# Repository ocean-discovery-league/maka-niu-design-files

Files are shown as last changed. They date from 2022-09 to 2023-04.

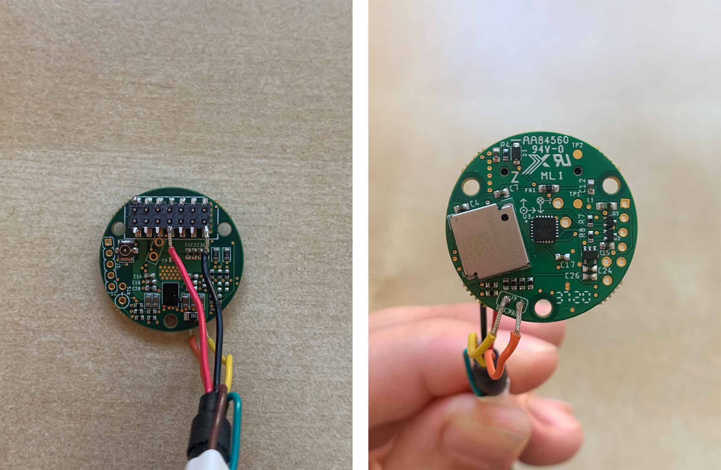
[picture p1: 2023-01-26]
Circuit_Boards/endcap/GNSS_AND_IMU_FIX/GNSS_Flashing_Example.jpg

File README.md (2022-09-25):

# maka-niu-design-files
All files needed to build a Maka Niu

Instructions for fabrication and software installation here.

Link to install image here.
 
Please direct all questions concerning fabrication plans or direct purchase of the Delrin housing to Dr. Allan Adams of Oceanic Labs (allan@oceanic-labs.org)

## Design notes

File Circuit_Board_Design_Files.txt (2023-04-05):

To build a Maka Niu Camera system, you will need to acquire a Pi Zero W or a Pi Zero 2W
Additionally, you will need to acquire or fabricate the following custom PCBs

-Endcap PCB
-Battery Management PCB
-Pi Zero Shield
-Hall Sensor Board (aka Hall Ring)

To build a Maka Niu LED module, you will need to acquire a Pi Zero W or a Pi Zero 2W
Additionally, you will need to acquire or fabricate the following custom PCBs

-Endcap PCB
-Battery Management PCB
-Pi Zero Shield
-Hall Sensor Board (aka Hall Ring)
-LED PCB

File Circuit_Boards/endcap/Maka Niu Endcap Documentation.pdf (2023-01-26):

### Maka-Niu Endcap PCB

The endcap PCB is a 6-layer, 26mm diameter board that handles wireless Qi charging, GPS (including external antenna connector), IMU, and breakouts for the Keller pressure sensor and for an external thermistor to provide temperature-related shutdown capability.

The endcap PCB connects to the other PCBs in the stack via a 14 pin Molex connector.

The wireless charging IC is an IDT P9221-R. The datasheet can be found here: https://www.mouser.com/datasheet/2/464/IDT_P9221-R-Datasheet_DST_20171010-1093280.pdf (https://www.mouser.com/datasheet/2/464/IDT_P9221-R-Datasheet_DST_20171010-1093280.pdf)

The GPS module is an AirPrime XM1110. The most recent datasheet must be requested from Sierra Wireless.

The IMU is a TDK InvenSense ICM-20948 9-axis IMU. The datasheet can be found here: https://invensense.tdk.com/wp-content/uploads/2016/06/DS-000189-ICM-20948-v1.3.pdf

Following are the layouts of the top and bottom of the board:

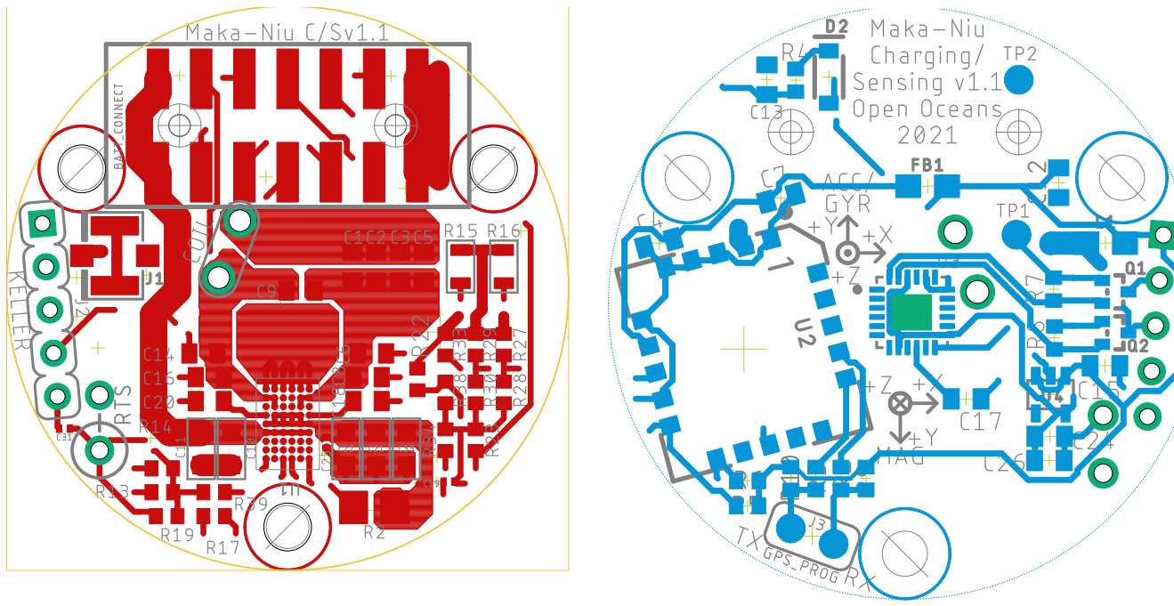
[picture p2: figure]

Top of board, important details

The pinouts for the 14 pin Molex connector are as follows:

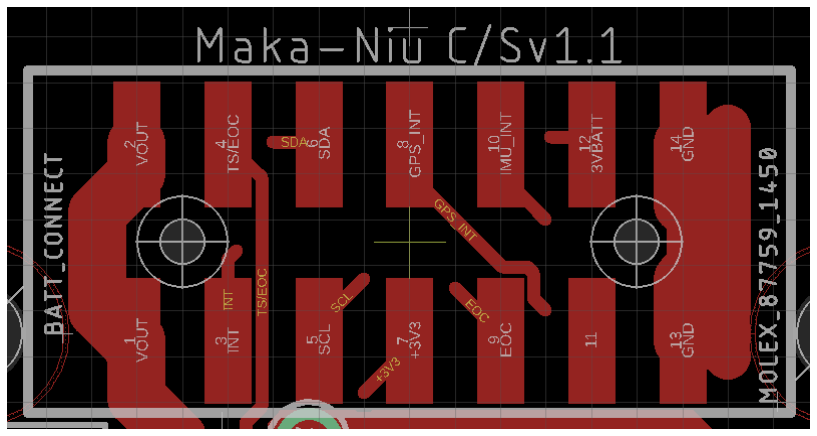
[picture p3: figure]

Pins numbered according to columns left to right and rows bottom to top within columns (as shown in diagram above, viewed in this orientation):

1: VOUT (to main battery)
2: VOUT (to main battery)
3: !INT (for wireless charger)
4: TS/EOC (temperature sensing/end of charge for wireless charger) 5: SCL
6: SDA
7: +3.3V
8: GPS INTERRUPT
9: EOC (from Keller pressure sensor) 10: IMU INTERRUPT
11: unused
12: 3V BACKUP BATTERY (for GPS)
13: GND (common)
14: GND (common)

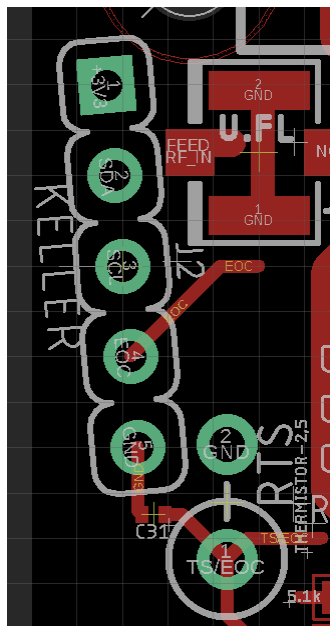
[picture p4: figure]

The pinouts for the Keller pressure sensor and the thermistor are as follows:

For the Keller sensor, where pin 1 has the square pad:

1: +3.3V
2: SDA
3: SCL
4: EOC
5: GND

For the thermistor, where pin 1 is circled:

1: TS/EOC
2: GND

Here is the ECAD layout of the full top of the board:

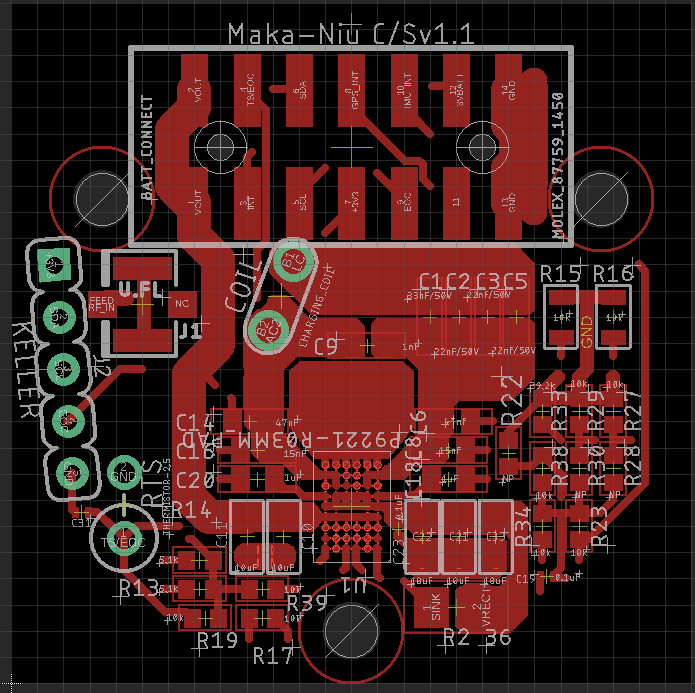
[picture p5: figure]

Important programming resistors to note in the resistor cluster to the bottom right:

R22: used as part of a resistor divider for setting the overcurrent limit (ILIM)
R28: used as part of a resistor divider for tuning foreign object detection (FOD); tunes received packet power gain (RPPG)
R30: used as part of a resistor divider for tuning foreign object detection (FOD); tunes received packet power offset (RPPO)

These resistors are unpopulated in the initial assembly.

Here is a photograph of the prototype assembly. The unpopulated resistors are visible in the lower right, although they are not labeled on the silkscreen. They will be labeled in the final production run.

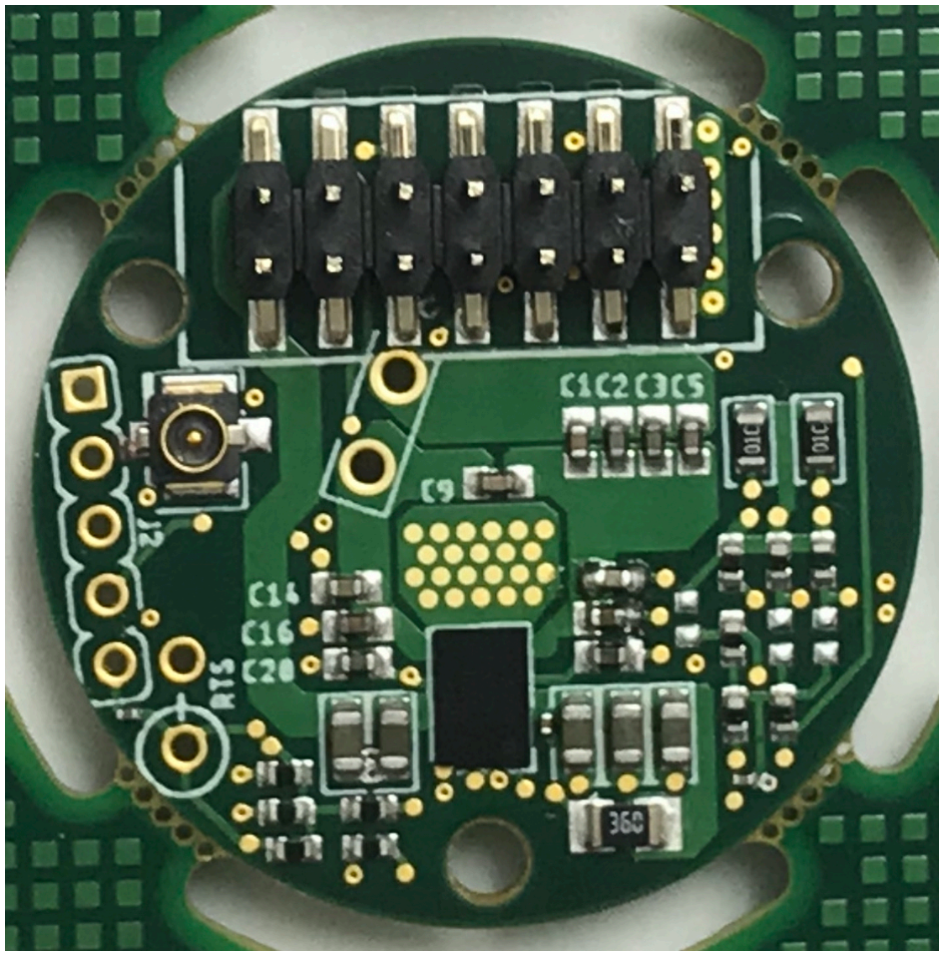
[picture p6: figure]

Bottom of board, important details

The bottom of the board contains the GPS module and the IMU. The important features for manual adjustment/testing are J3, the GPS programming connector, and the two electrical testpoints TP1 and TP2.

Here is the ECAD layout of the bottom of the board:

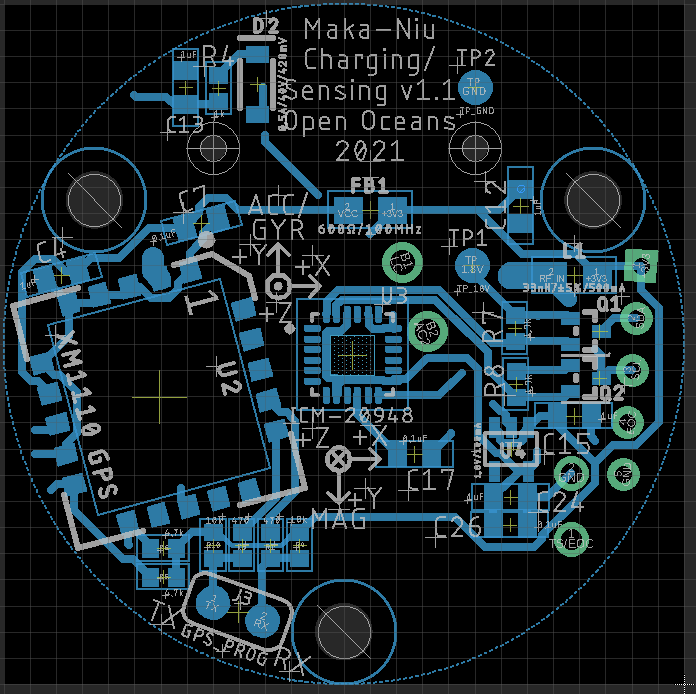
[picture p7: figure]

As can be seen from this image, J3 has TX on the left and RX on the right.

The expected testpoint voltages are as follows:

TP1: +1.8V
TP2: GND

Here is a photograph of the prototype assembly. Note that TX and RX are unlabeled in the silkscreen; they will be labeled in the final production run. Note also that the GPS module is 180° rotated from its correct orientation; this photograph was taken before this assembly error was corrected. It will be correctly oriented in the production run.

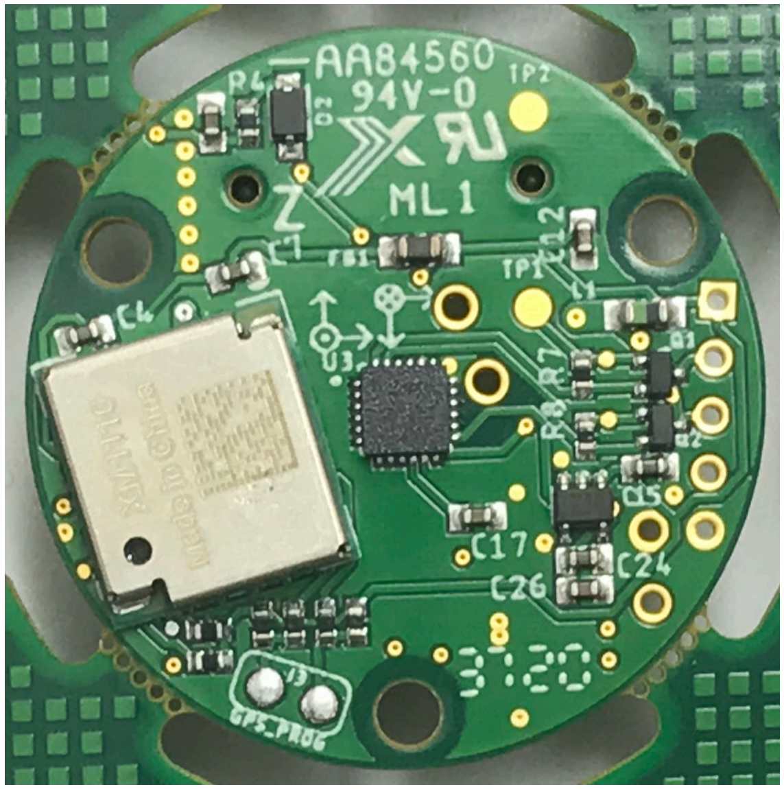
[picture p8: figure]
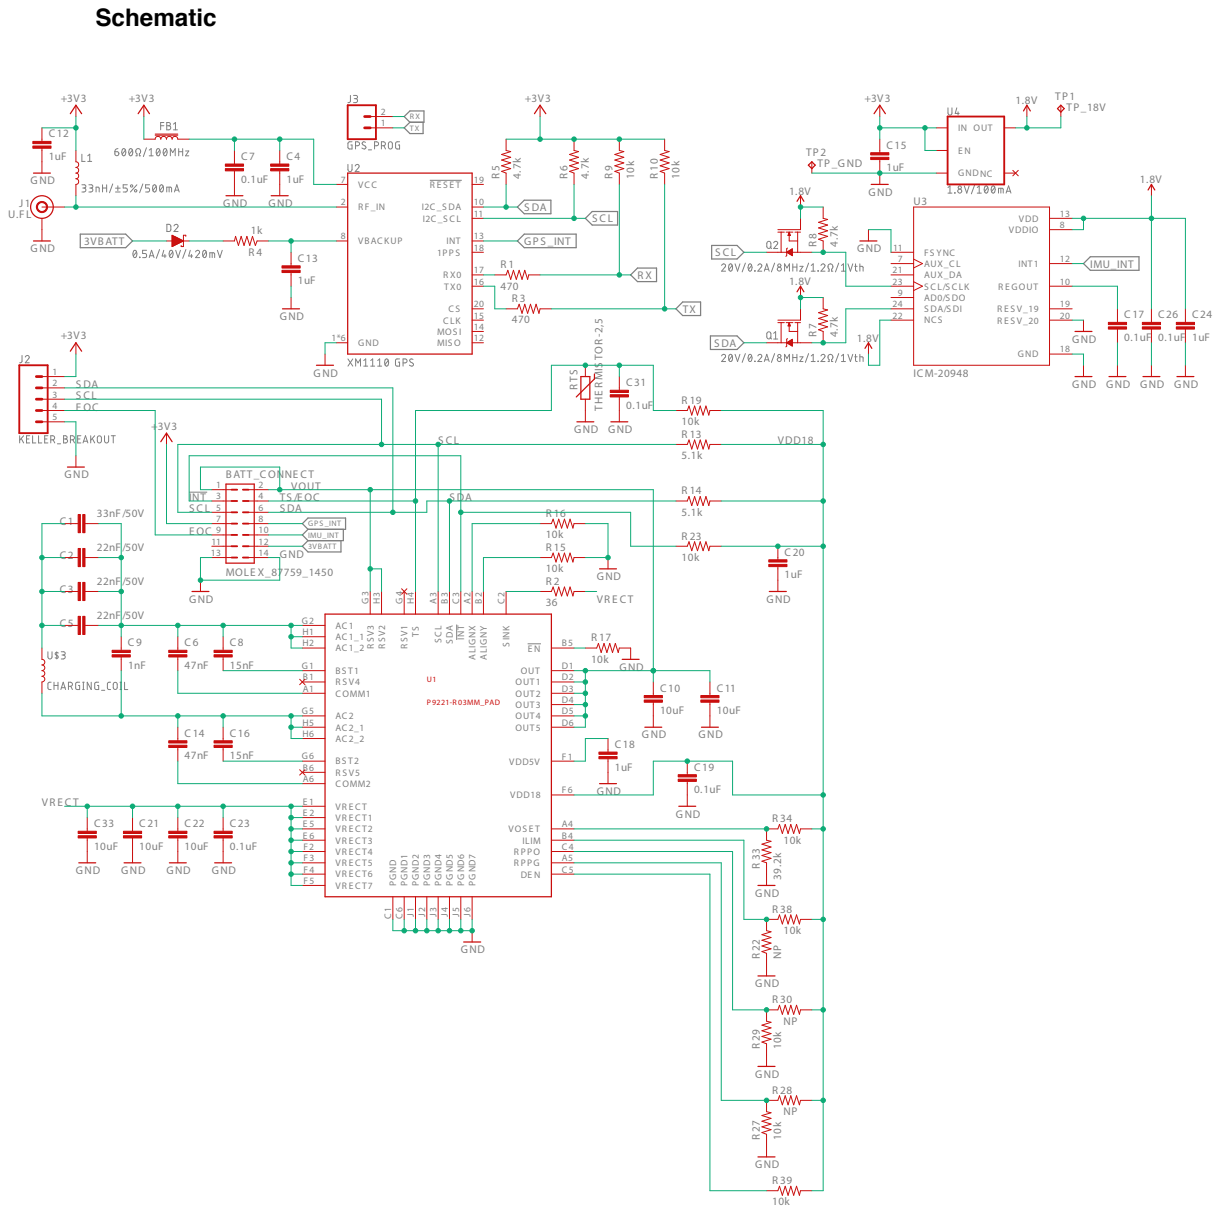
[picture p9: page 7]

GND GND

BS T1 G1 | 10k GND
R S V4 B1 COMM1 A1 | | GND

AC2_1 H5
AC2_2 H6 | GND

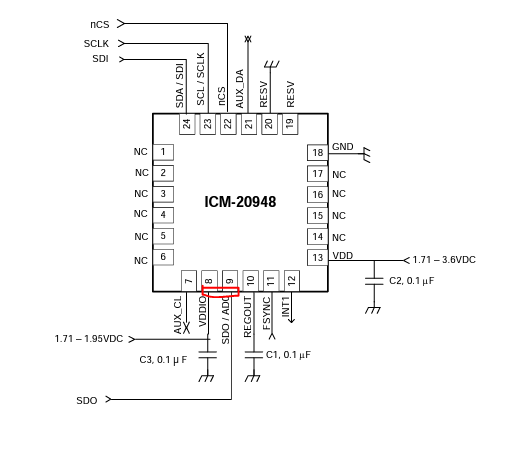
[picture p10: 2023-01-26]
Circuit_Boards/endcap/GNSS_AND_IMU_FIX/IMU_pin_to_short.png

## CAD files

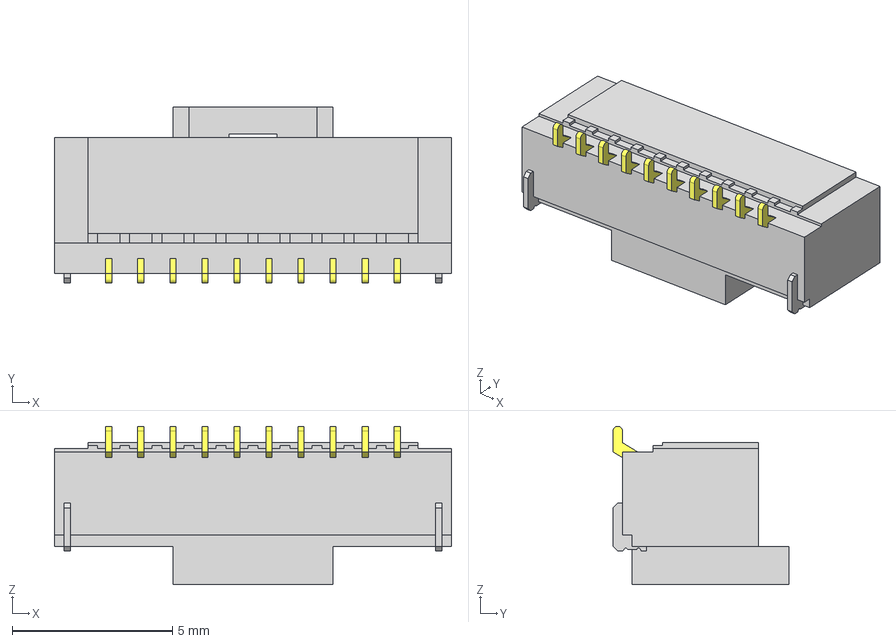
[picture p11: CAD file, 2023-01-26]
Circuit_Boards/battery_manager_V1.1/T1M-10-F-SV-L.stp
12.4 x 5.50 x 4.95 mm
P2T1M-10-T-SV-L
T1T1M-10-T-SV-L

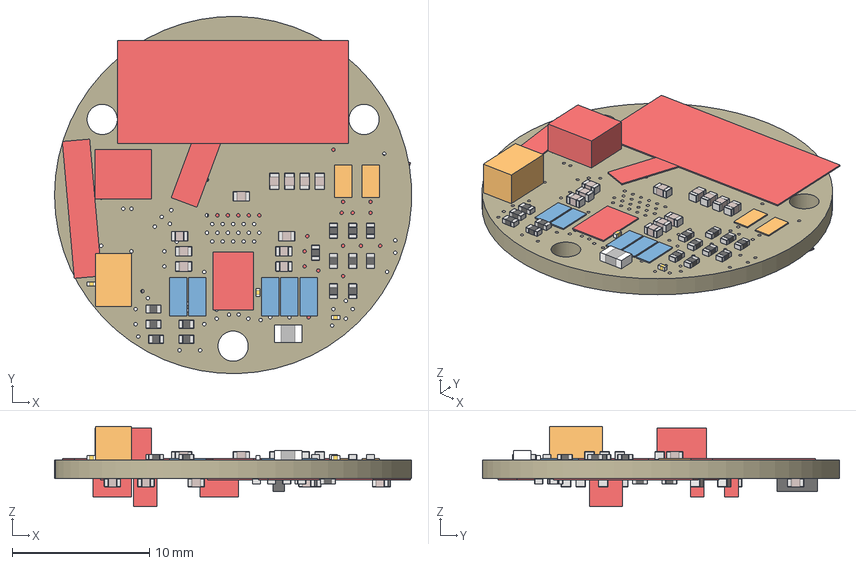
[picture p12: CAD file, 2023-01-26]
Circuit_Boards/endcap/Maka Niu Endcap.step
26.0 x 26.0 x 5.85 mm
Board
MOLEX_87759_1450
1nF x 19
10uF x 5
0.1uF x 3
0.5A/40V/420mV
33nH/±5%/500mA x 2
U.FL
KELLER_BREAKOUT
GPS_PROG
20V/0.2A/8MHz/1.2Ω/1Vth x 2
NP x 23
10k x 2
THERMISTOR-2,5
CHARGING_COIL
P9221-R03MM_PAD
XM1110 GPS
ICM-20948
1.8V/100mA

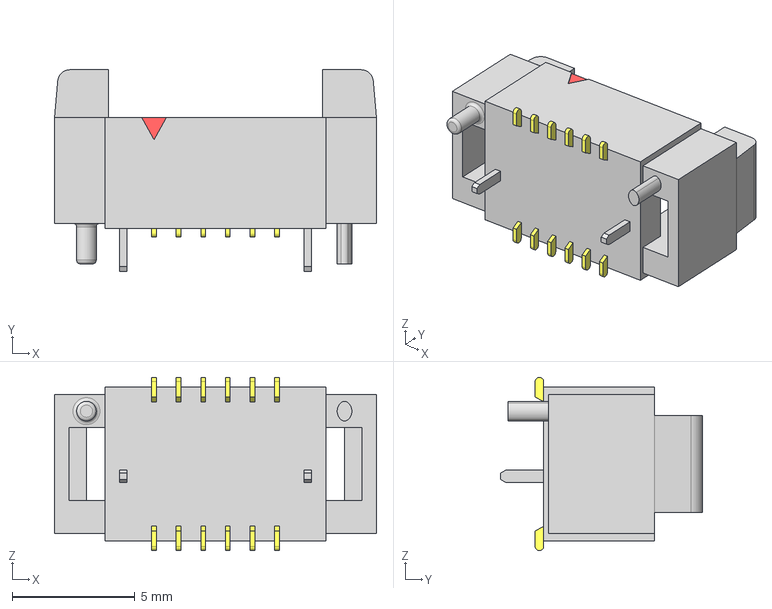
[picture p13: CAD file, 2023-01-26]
Circuit_Boards/hall_ring_V2/T1M-06-GF-DV.stp
13.1 x 8.20 x 7.05 mm
_T1T1M-06-T-DV
_P2T1M-06-T-DV

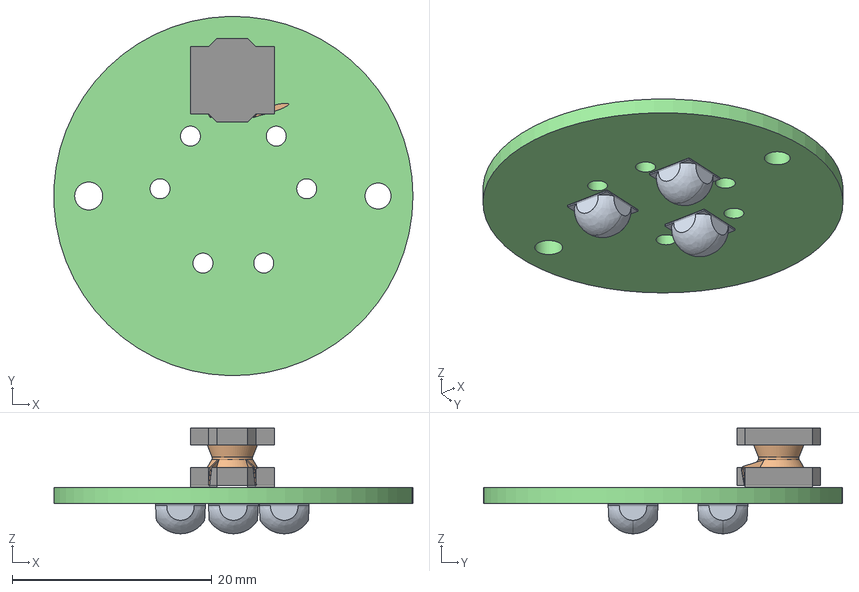
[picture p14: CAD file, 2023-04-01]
Circuit_Boards/LED_board_B/LED_board.step
36.0 x 36.0 x 10.6 mm
LED_board PCB

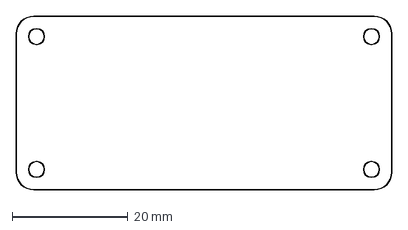
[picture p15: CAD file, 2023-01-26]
Circuit_Boards/wireless_charger/charger_outline.dxf
65.0 x 30.0 mm

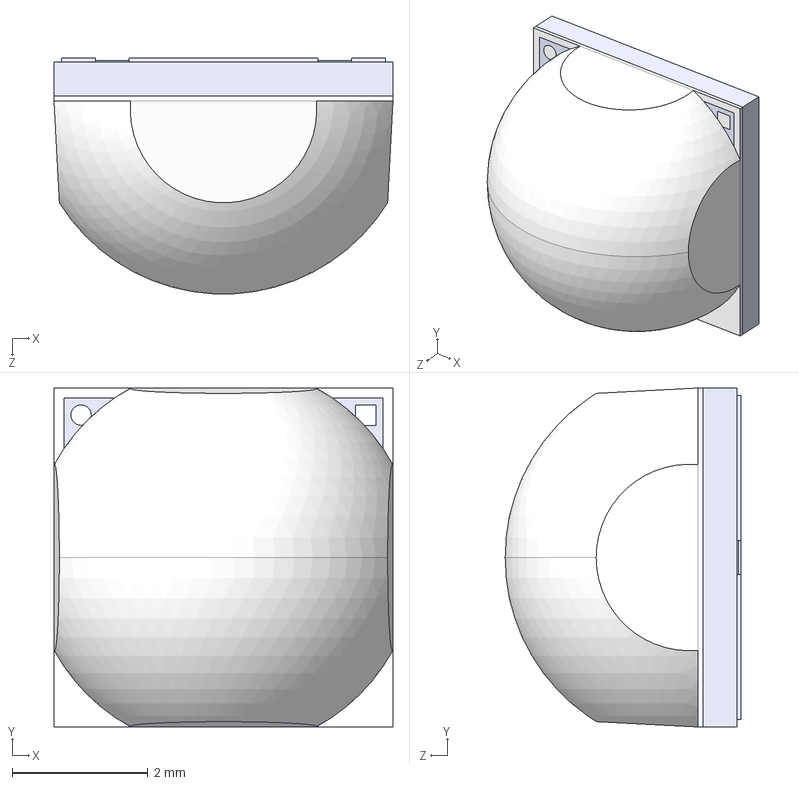
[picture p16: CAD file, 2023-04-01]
Circuit_Boards/LED_board_B/Cree LED XLamp XHP50.2.STEP
5.00 x 5.00 x 3.48 mm
2500-00676-C.stp
2500-00676-BT.stp
2500-00676-SMB.stp
2500-00676-SMB1.stp
2500-00676-TT.stp
2500-00676-TS.stp
2610-00073-DOME.stp

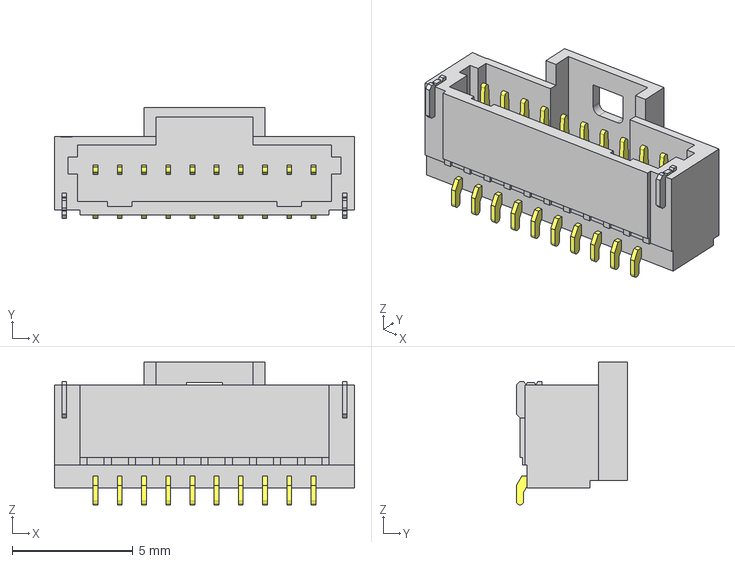
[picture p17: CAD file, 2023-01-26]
Circuit_Boards/pi_zero_shield/T1M-10-F-SH-L-K.step
12.4 x 4.60 x 5.90 mm
_T1T1M-10-T-SH-L
_P2T1M-10-T-SH-L

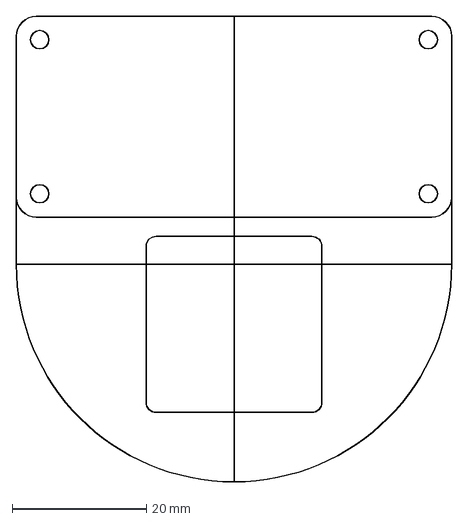
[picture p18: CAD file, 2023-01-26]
Circuit_Boards/wireless_charger/charger_outline_large.dxf
65.0 x 69.5 mm

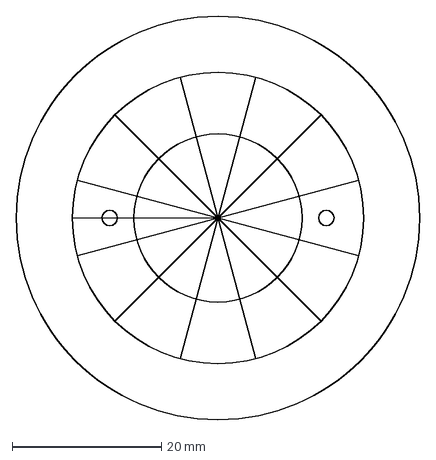
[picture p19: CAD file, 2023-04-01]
Circuit_Boards/LED_board_B/LED_board_expose.dxf
54.0 x 54.0 mm

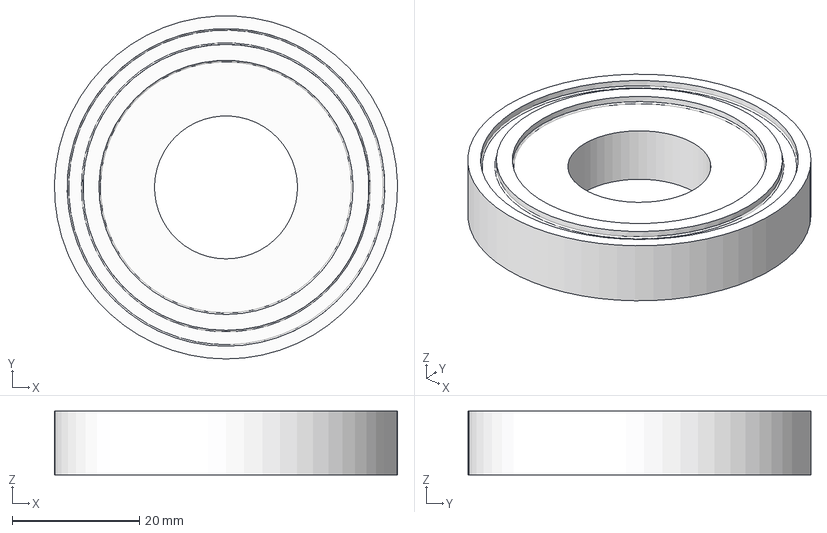
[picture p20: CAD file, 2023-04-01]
Circuit_Boards/LED_board_B/LED_Heatsink_1.1.16.step
54.0 x 54.0 x 10.0 mm

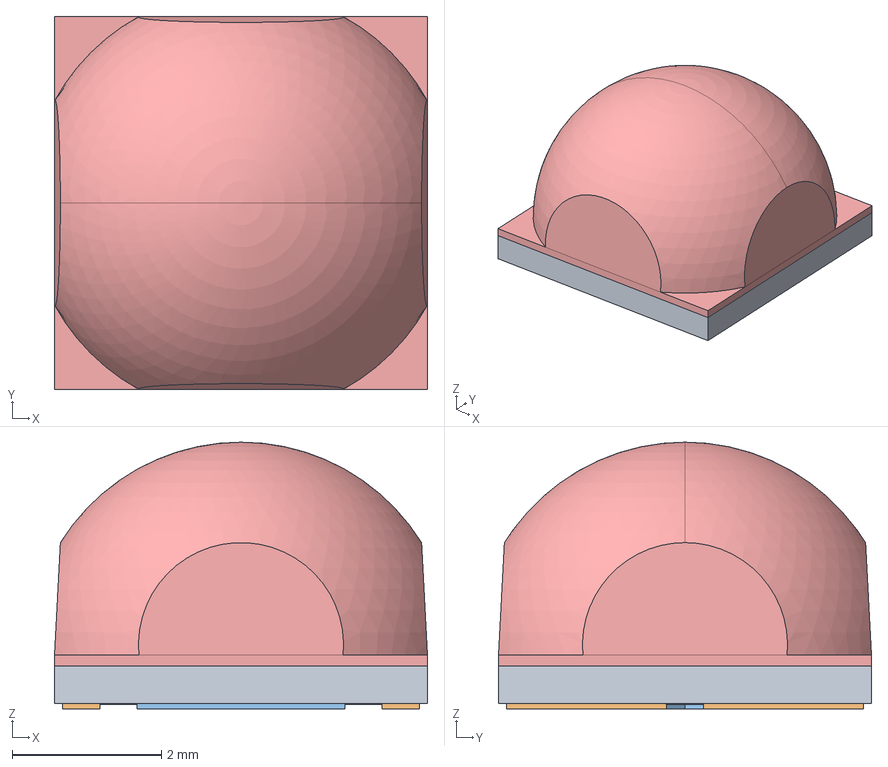
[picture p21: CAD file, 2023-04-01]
Circuit_Boards/LED_board_B/XHP50.stp
5.00 x 5.00 x 3.58 mm
2500-00513-CERAMIC
2500-00513-BOTTOM-TRACE
2500-00513-SOLDERMASK-NONOTCH
2500-00513-SOLDERMASK-BACK
2500-00513-TOP-TRACE
2500-00513-TOP-SOLDERMASK
2_85_TRUNCATED_DOME

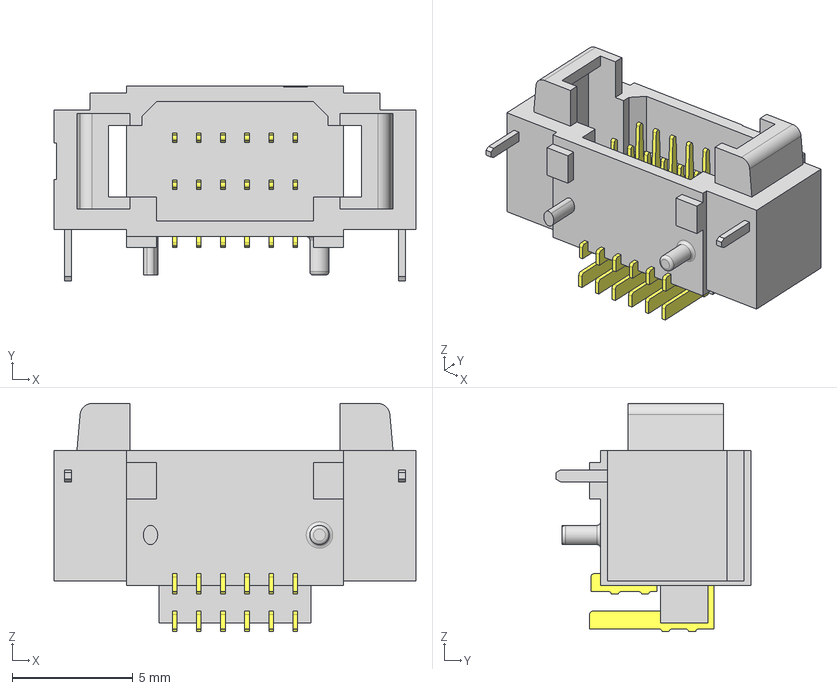
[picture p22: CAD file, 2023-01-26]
Circuit_Boards/pi_zero_shield/T1M-06-GF-DH.step
15.0 x 8.10 x 9.45 mm
_T1T1M-06-T-DH
_P2T1M-06-T-DH

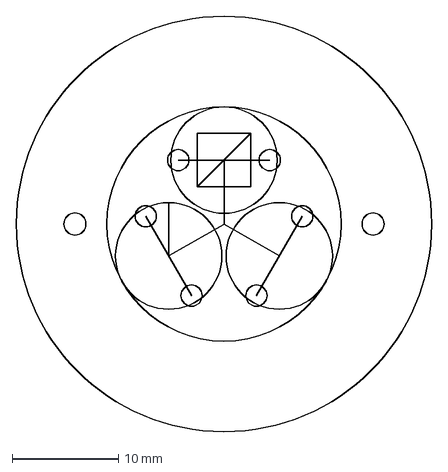
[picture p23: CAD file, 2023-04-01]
Circuit_Boards/LED_board_B/LED_board_outline.dxf
39.0 x 39.0 mm

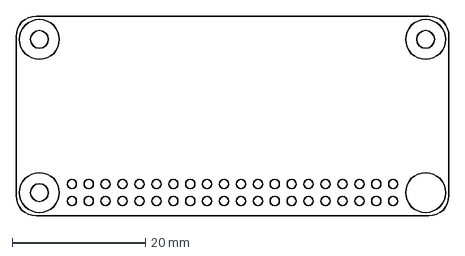
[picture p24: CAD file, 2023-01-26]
Circuit_Boards/pi_zero_shield/shield.dxf
65.0 x 30.0 mm

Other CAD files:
Circuit_Boards/pi_zero_shield/T1M-10-F-SV-L.stp
Circuit_Boards/pi_zero_shield/m20-7812045_asm.stp

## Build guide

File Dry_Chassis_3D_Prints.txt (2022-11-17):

To build the dry chassis of a Maka Niu Camera system, you will need to 3D print the following components

-Chassis_Battery_Cartridge
-Chassis_Compute_Stack_Adapter
-Chassis_PiCam_Adapter
-Chassis_PiCam_Black_Shield (We suggest print in black)
-Battery_contact_adapter
-Endcap_spacer

To build the dry chassis of a Maka Niu LED module, you will need to 3D print the following components
-Chassis_Battery_Cartridge
-Chassis_Compute_Stack_Adapter
-Chassis_LED_Adapter
-Battery_contact_adapter
-Endcap_spacer

All STL files can be viewed and downloaded at 
https://drive.google.com/drive/folders/1nLOXgDBbGBHkGrNHWlzP19P_V9sPvfNX?usp=share_link

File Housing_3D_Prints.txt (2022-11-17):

The housing requires machined components, and several additional 3D printed components.
For the machining files, see Housing_Machining_Drawings.txt.
The 3D printed components below provide the control interface and rigging hardware

To build a Maka Niu Camera system, you will need to 3D print the following components:
-Fixed_Dial
-Rotating_Dial
-Spring_Button
-Lens_Cap
-Faceplate_CoilPuck
-Rear_Lock

To build a Maka Niu LED module, you will need to 3D print the following components
-Fixed_Dial
-Rotating_Dial_LED_version
-Spring_Button
-Lens_Cap
-Faceplate_CoilPuck
-Rear_Lock

All STL files can be viewed and downloaded at 
https://drive.google.com/drive/folders/1u39a1h19gjNEHflURePqkqqbymbViMll?usp=share_link

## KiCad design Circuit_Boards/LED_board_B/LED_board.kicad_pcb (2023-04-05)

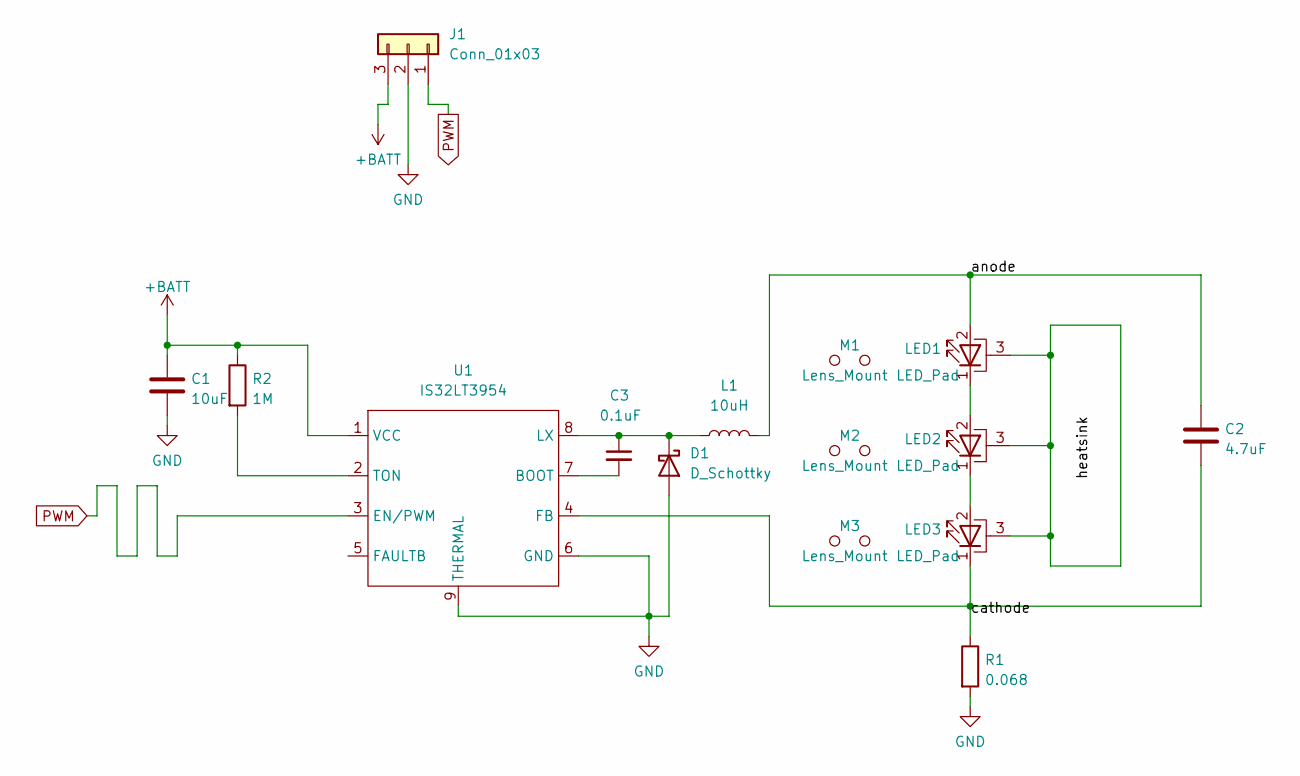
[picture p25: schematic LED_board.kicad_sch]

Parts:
C1: 10uF; C_1210_3225Metric; Digikey 13-CC1210KFX7R8BB106CT-ND
C2: 4.7uF; C_1210_3225Metric; Digikey 1276-1292-1-ND
C3: 0.1uF; C_0603_1608Metric; Digikey 1276-1935-1-ND
D1: D_Schottky; D_SMA; Digikey SK54A-LTPMSCT-ND
J1: Conn_01x03; Molex_Micro-Fit_3.0_43650-0324_1x03-1MP_P3.00mm_Vertical; Digikey WM3887CT-ND
L1: 10uH; PA5175_Inductor; Digikey 553-PA5175.103NLTCT-ND
LED1, LED2, LED3: LED_Pad; LED_Cree-XHP50_3V_hand_solder; Digikey XMLBWT-00-0000-0000U2050CT-ND
M1, M2, M3: Lens_Mount; LEDiL_Clip; Digikey 711-FP18200_LISA3-M-CLIP16-ND
R1: 0.068; R_2512_6332Metric; Digikey 311-0.068TCT-ND
R2: 1M; R_0603_1608Metric; Digikey RMCF0603FG1M00CT-ND
U1: IS32LT3954; SOP-8-1EP_4.57x4.57mm_P1.27mm_EP4.57x4.45mm_ThermalVias; Digikey 2521-IS32LT3954-GRLA3-TRCT-ND

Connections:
+BATT: C1.1, J1.3, R2.1, U1.1 (VCC)
/anode: C2.1, L1.2, LED1.2 (A)
/cathode: C2.2, LED3.1 (K), R1.1, U1.4 (FB)
/heatsink: LED1.3 (PAD), LED2.3 (PAD), LED3.3 (PAD)
GND: C1.2, D1.2 (A), J1.2, R1.2, U1.6 (GND), U1.9 (THERMAL)
unnamed: C3.1, D1.1 (K), L1.1, U1.8 (LX)
unnamed: C3.2, U1.7 (BOOT)
unnamed: LED1.1 (K), LED2.2 (A)
unnamed: LED2.1 (K), LED3.2 (A)
unnamed: R2.2, U1.2 (TON)
PWM: J1.1, U1.3 (EN/PWM)

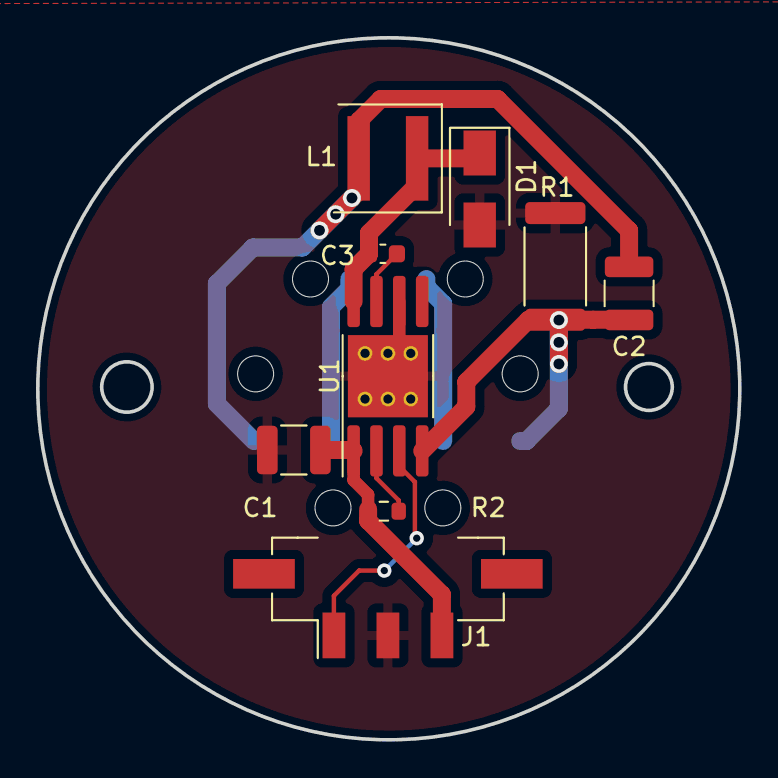
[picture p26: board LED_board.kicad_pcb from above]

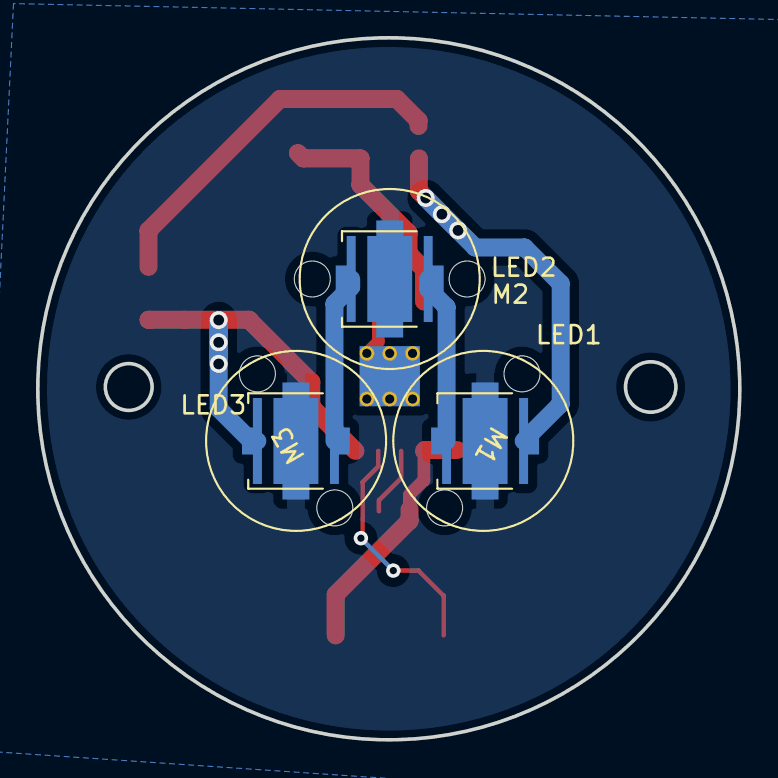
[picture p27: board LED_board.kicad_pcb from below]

Board: 2 copper layers, 39.0 x 39.0 mm, 15 parts (6 on the bottom side), 11 nets.

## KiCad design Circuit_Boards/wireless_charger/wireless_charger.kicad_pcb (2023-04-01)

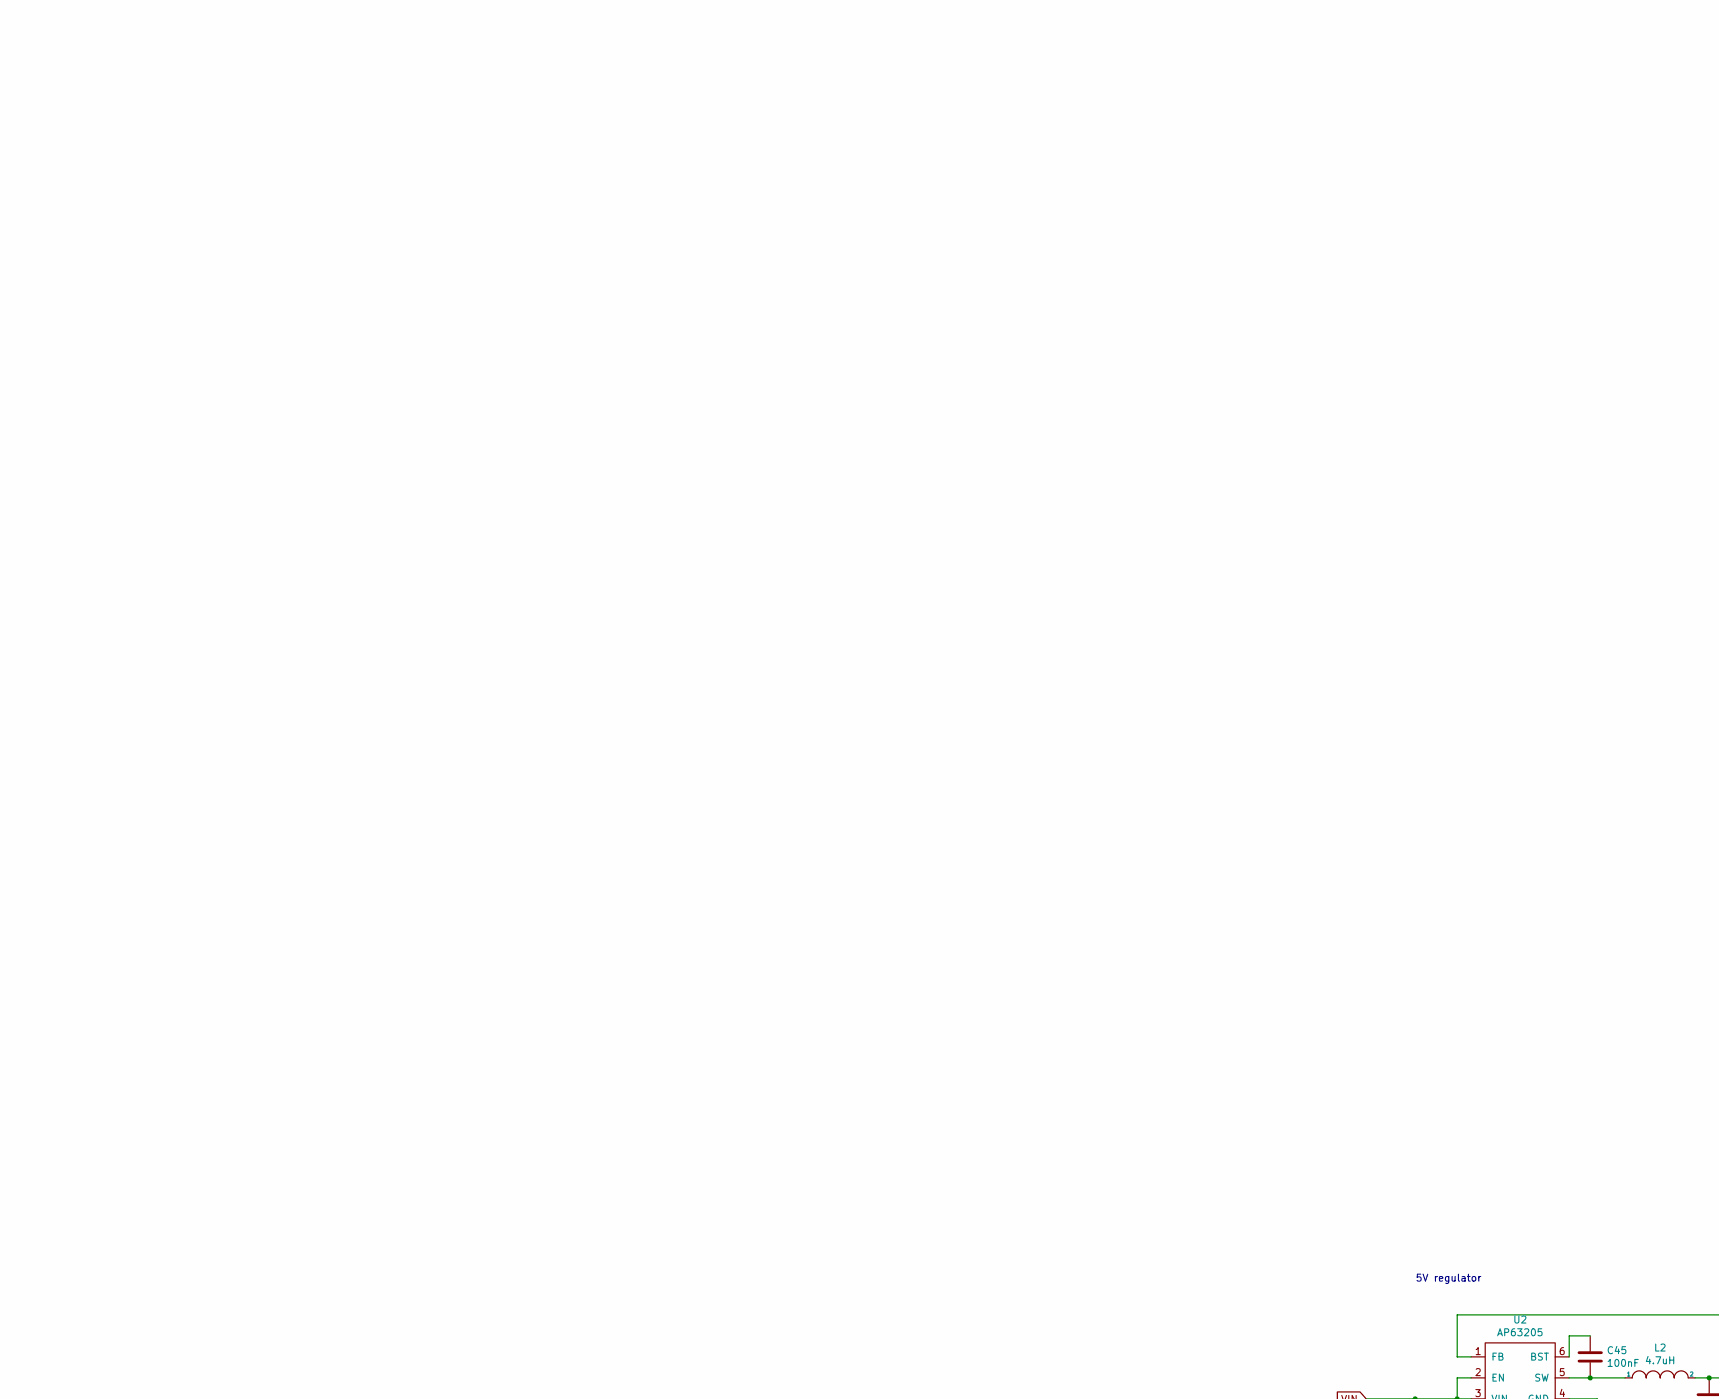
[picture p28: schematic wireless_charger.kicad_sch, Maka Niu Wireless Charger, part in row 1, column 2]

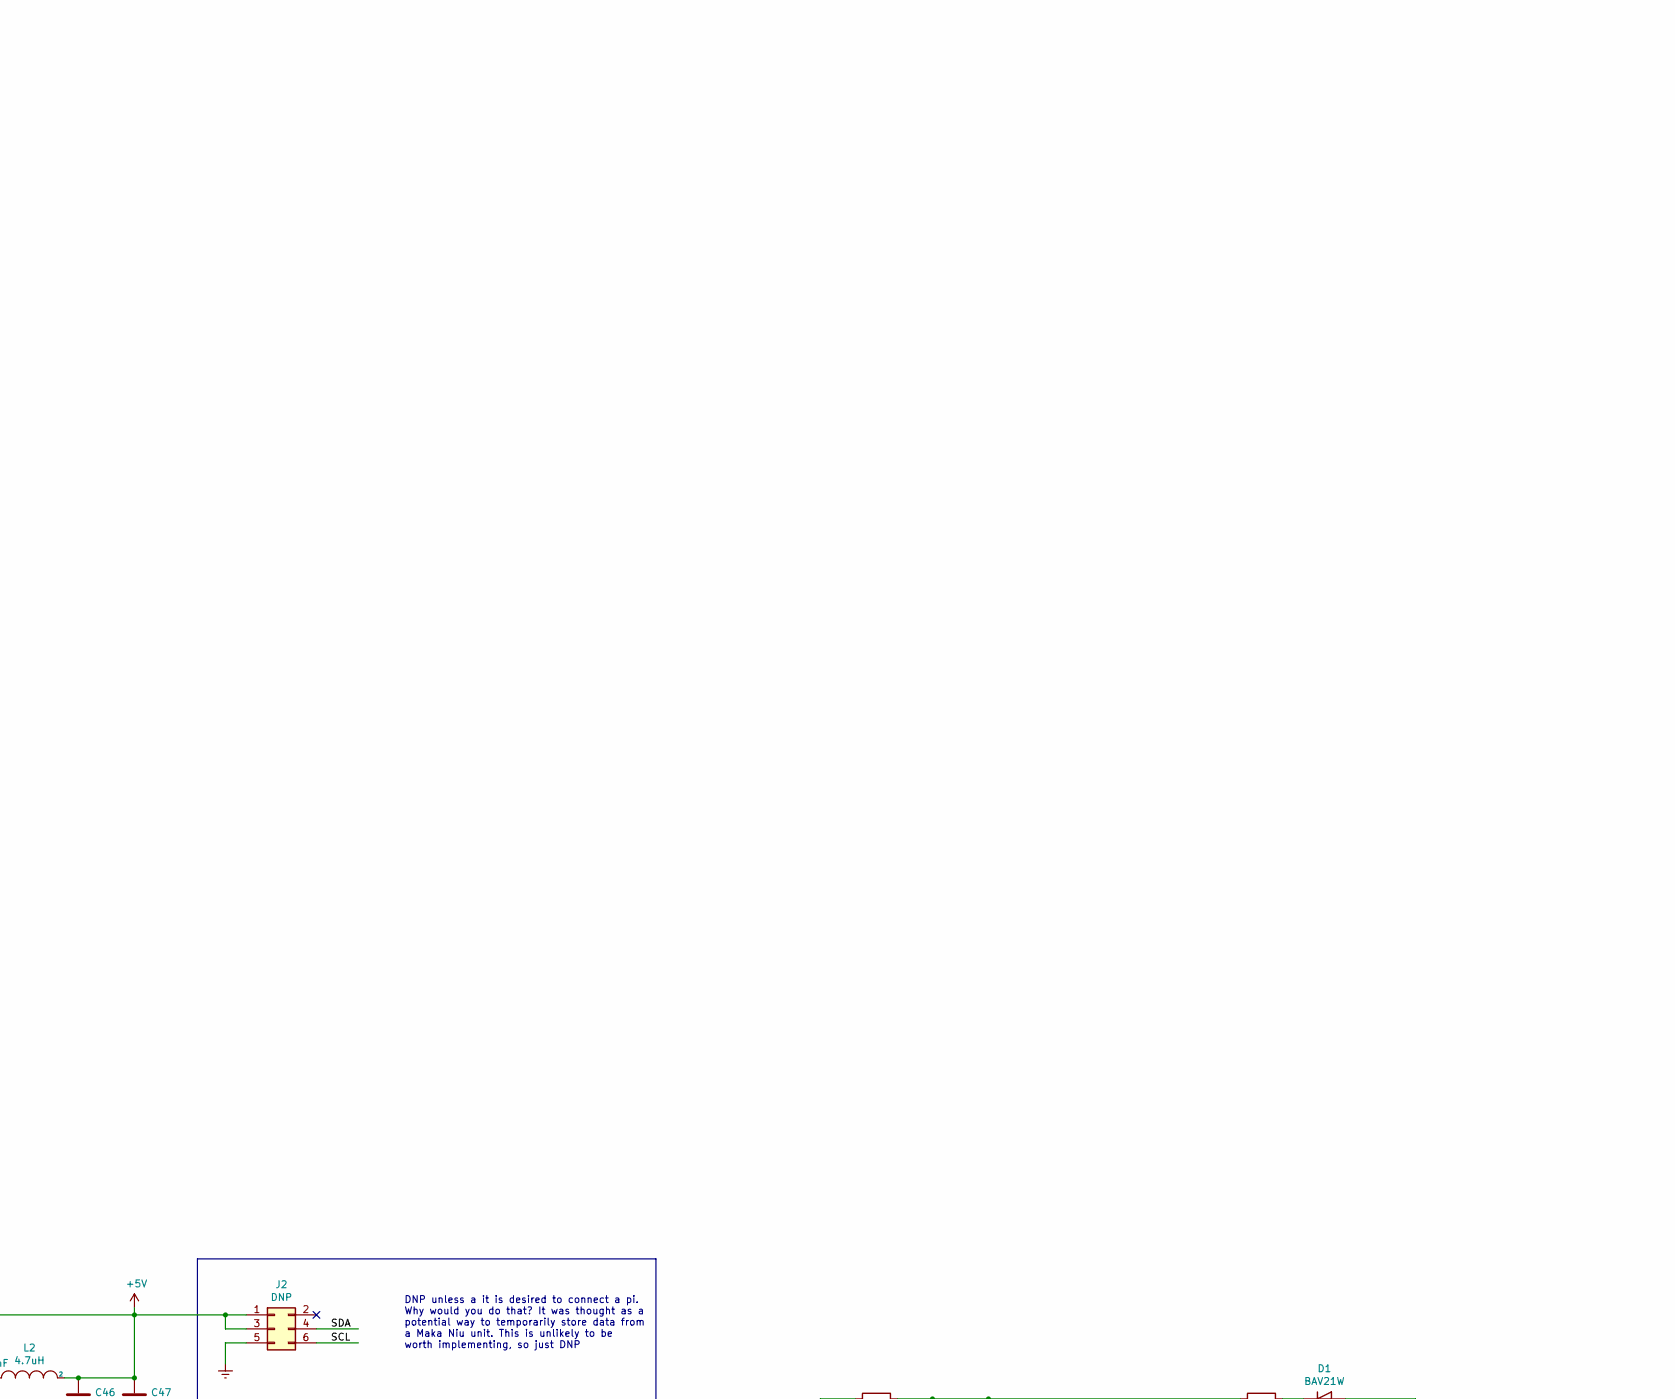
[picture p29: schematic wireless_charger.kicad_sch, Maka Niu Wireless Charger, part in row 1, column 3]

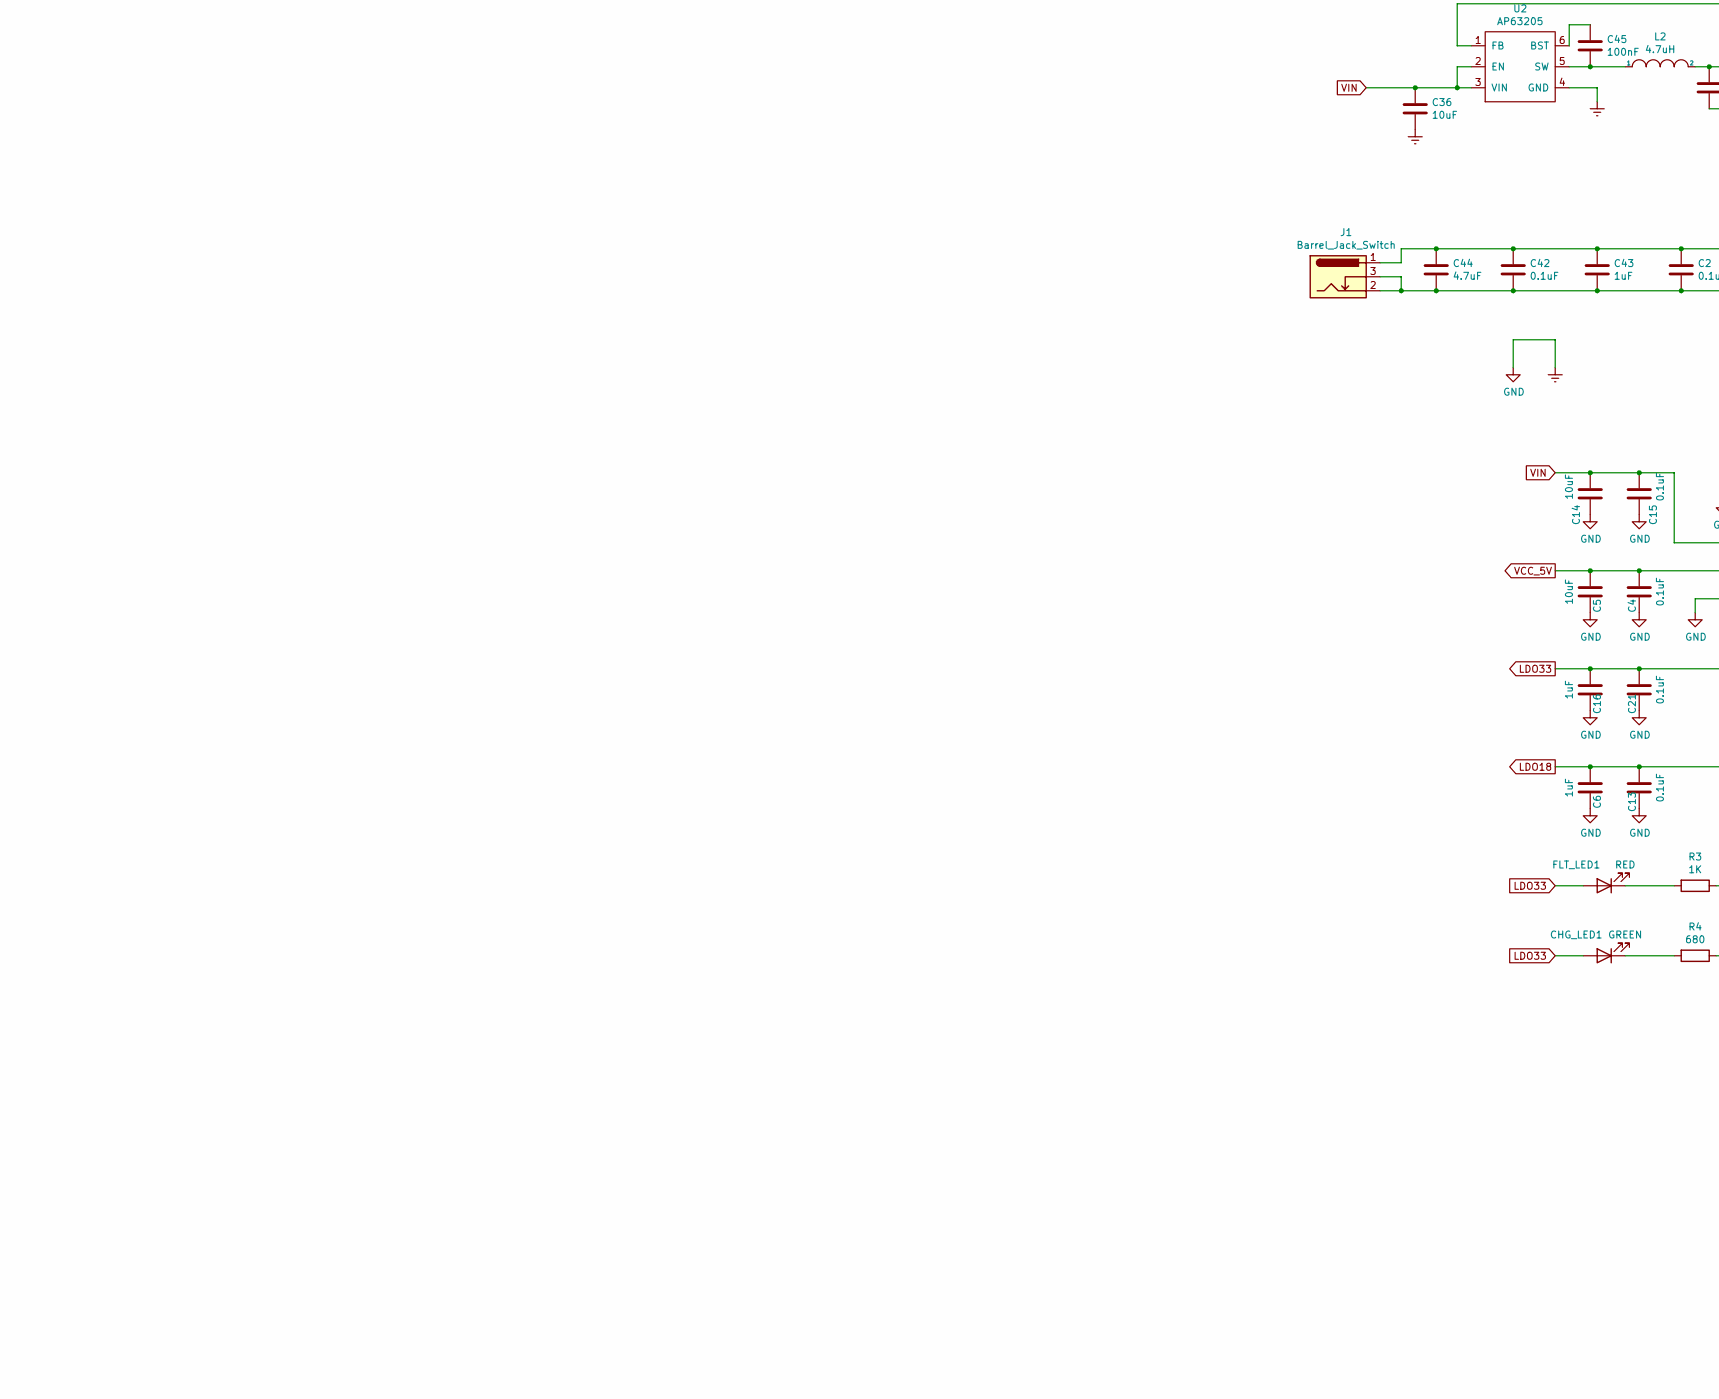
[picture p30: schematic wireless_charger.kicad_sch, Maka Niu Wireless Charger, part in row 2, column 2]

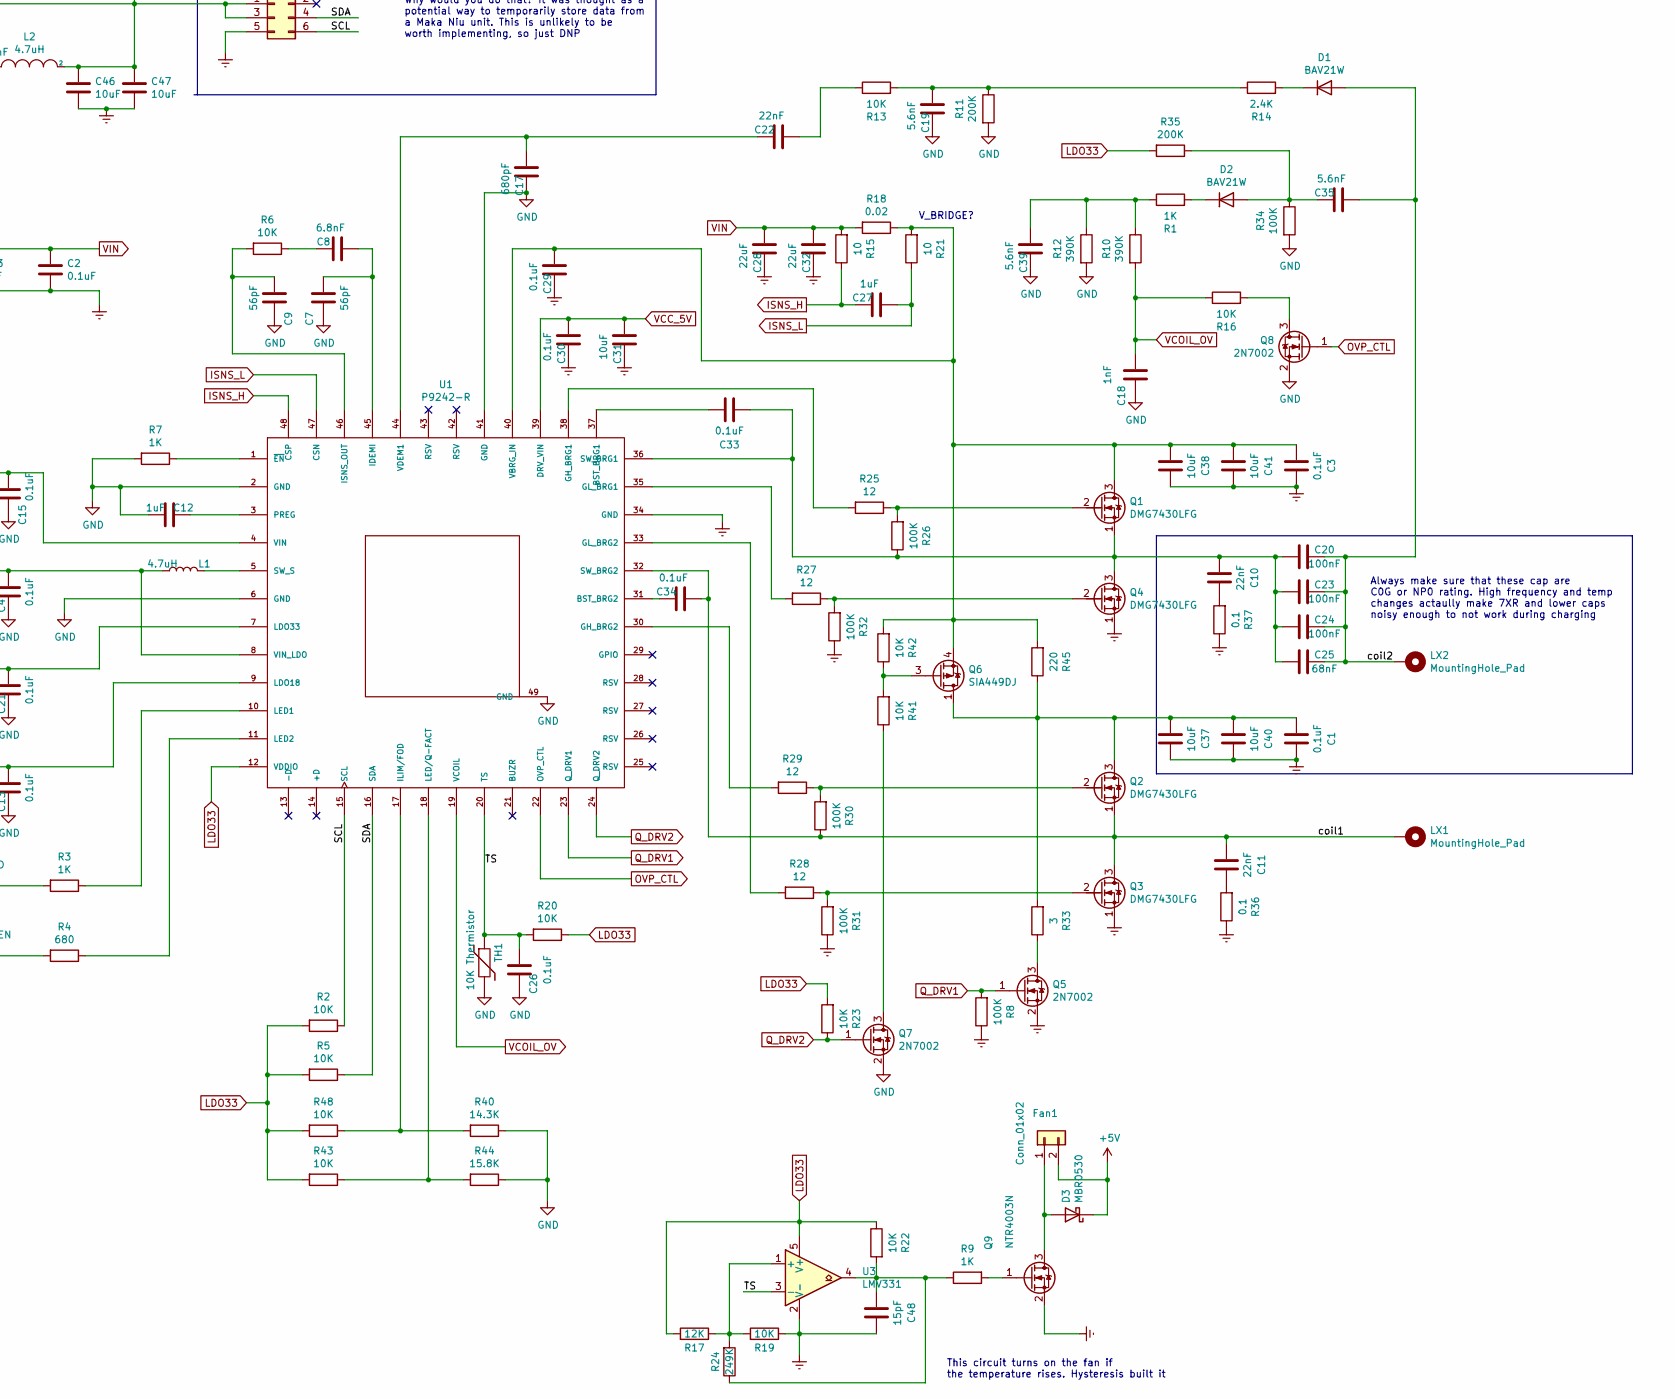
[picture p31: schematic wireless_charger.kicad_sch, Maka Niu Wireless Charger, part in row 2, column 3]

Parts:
C1, C2, C3, C4, C13, C15, C21, C26, C29, C30, C33, C34: 0.1uF; C_0402_1005Metric; Part Number ‎GRM155R71E104KE14D‎; Digikey 490-10698-1-ND
C5, C14, C31, C36, C37, C38, C40, C41, C46, C47: 10uF; C_0603_1608Metric; Part Number ‎GRM188R61E106KA73D; Digikey 490-18214-1-ND
C6, C12, C16, C27: 1uF; C_0402_1005Metric; Part Number ‎CC0402KRX5R8BB104; Digikey 311-1697-1-ND
C7, C9: 56pF; C_0402_1005Metric; Part Number ‎CC0402FRNPO9BN560; Digikey 311-3734-1-ND
C8: 6.8nF; C_0402_1005Metric; Part Number ‎GCM155R71E682KA37D‎; Digikey 490-17758-1-ND
C10, C11: 22nF; C_0603_1608Metric; Part Number CC0603KRX7R9BB223; Digikey 311-1370-1-ND
C17: 680pF; C_0402_1005Metric; Part Number ‎CC0402KRX7R9BB681; Digikey 311-1030-1-ND
C18: 1nF; C_0603_1608Metric; Part Number CL10B102KB8WPJC; Digikey 1276-CL10B102KB8WPJCTR
C19, C35, C39: 5.6nF; C_0603_1608Metric; Part Number ‎C1608C0G2A562J080AE‎; Digikey 445-180278-1-ND
C20, C23, C24: 100nF; C_1206_3216Metric; Part Number ‎GRM31C5C2A104JA01L‎; Digikey 490-16315-1-ND
C22: 22nF; C_0402_1005Metric; Part Number ‎GRM155R71H223KA12J‎; Digikey 490-6360-1-ND
C25: 68nF; C_1206_3216Metric; Part Number ‎C3216C0G2A683J160AC; Digikey 445-172675-1-ND
C28, C32: 22uF; C_1206_3216Metric; Part Number ‎CL31A226KAHNNNE; Digikey 1276-3047-1-ND
C42: 0.1uF; C_0603_1608Metric; Part Number ‎CC0603KPX7R9BB104‎; Digikey 311-3567-1-ND
C43: 1uF; C_0603_1608Metric; Part Number ‎CL10A105KA8NNNC; Digikey 1276-1102-1-ND
C44: 4.7uF; C_0603_1608Metric; Part Number CAP CER 4.7UF 25V X5R 0603; Digikey 490-7203-1-ND
C45: 100nF; C_0603_1608Metric; Part Number CL10B104KB8NNNL; Digikey 1276-CL10B104KB8NNNLTR
C48: 15pF; C_0402_1005Metric; Part Number ‎CC0402GRNPO9BN150‎; Digikey 311-1649-1-ND
CHG_LED1: GREEN; LED_0603_1608Metric; Part Number LTST-S270KGKT; Digikey 160-1478-1-ND
D1, D2: BAV21W; D_SOD-123; Part Number ‎BAV21W-7-F‎; Digikey BAV21W-7-F‎
D3: MBR0530; D_SOD-123; Part Number ‎MBR0530T1G; Digikey MBR0530T1GOSCT-ND
FLT_LED1: RED; LED_0603_1608Metric; Part Number LTST-S270EKT; Digikey 160-1474-1-N
Fan1: Conn_01x02; PinHeader_1x02_P2.54mm_Vertical; Digikey DNP
J1: Barrel_Jack_Switch; CUI_PJ-002AH; Part Number ‎PJ-002AH; Digikey CP-002AH-ND
J2: DNP; PinHeader_2x03_P2.54mm_Vertical; Part Number ‎PPTC032LFBN-RC‎; Digikey S7071-ND
L1: 4.7uH; L_0603_1608Metric; Part Number ‎LQM18PN4R7MFR; Digikey 490-12065-1-ND
L2: 4.7uH; L_1008_2520Metric; Part Number ‎DFE252012P-4R7M=P2‎; Digikey 490-10651-1-ND
LX1, LX2: MountingHole_Pad; TestPoint_THTPad_D2.0mm_Drill1.0mm; Digikey DNP
Q1, Q2, Q3, Q4: DMG7430LFG; TRANS_DMP3017SFGQ-7_b; Part Number ‎DMG7430LFG-7; Digikey DMG7430LFG-7‎
Q5, Q7, Q8: 2N7002; SOT-23; Part Number ‎2N7002KT1G; Digikey 2N7002KT1GOSCT-ND
Q6: SIA449DJ; Vishay_PowerPAK_SC70-6L_Single; Part Number ‎SIA449DJ-T1-GE3‎; Digikey SIA449DJ-T1-GE3CT-ND
Q9: NTR4003N; SOT-23; Part Number ‎NTR4003NT1G; Digikey NTR4003NT1GOSCT-ND
R1, R3, R7, R9: 1K; R_0402_1005Metric; Part Number ‎RC0402JR-071KL; Digikey 311-1.0KJRCT-ND
R2, R5, R6, R13, R16, R19, R20, R22, R23, R41, R42, R43, R48: 10K; R_0402_1005Metric; Part Number ‎RC0402FR-0710KL; Digikey 311-10.0KLRCT-ND
R4: 680; R_0402_1005Metric; Part Number ‎RC0402JR-07680RL; Digikey 311-680JRCT-ND
R8, R26, R30, R31, R32: 100K; R_0402_1005Metric; Part Number ‎ERJ-2GEJ104X; Digikey P100KJCT-ND
R10, R12: 390K; R_0603_1608Metric; Part Number ‎ERJ-3GEYJ394V‎; Digikey P390KGCT-ND
R11, R35: 200K; R_0603_1608Metric; Part Number ‎RC0603FR-07200KL; Digikey 311-200KHRCT-ND
R14: 2.4K; R_0402_1005Metric; Part Number ‎ERJ-2GEJ242X; Digikey P2.4KJCT-ND
R15, R21: 10; R_0402_1005Metric; Part Number ‎ERJ-2RKF10R0X; Digikey P10.0LCT-ND
R17: 12K; R_0402_1005Metric; Part Number RC0402FR-0712KL; Digikey 311-12.0KLRCT-ND
R18: 0.02; R_0805_2012Metric; Part Number ‎WSL0805R0200FEA‎; Digikey WSLA-.02CT-ND
R24: 249K; R_0402_1005Metric; Digikey CR0402-FX-2493GLFCT-ND
R25, R27, R28, R29: 12; R_0402_1005Metric; Part Number ‎ERJ-2GEJ120X; Digikey P12JCT-ND
R33: 3; R_0805_2012Metric; Part Number ‎RC0805FR-073RL; Digikey 311-3.00CRCT-ND
R34: 100K; R_0603_1608Metric; Part Number ‎ERJ-3EKF1003V; Digikey P100KHCT-ND
R36, R37: 0.1; R_0402_1005Metric; Part Number ‎ERJ-2BSJR10X‎; Digikey P17359CT-ND
R40: 14.3K; R_0402_1005Metric; Part Number CRCW040214K3FKED; Digikey 541-14.3KLTR-ND
R44: 15.8K; R_0402_1005Metric; Part Number RC0402FR-0715K8L; Digikey YAG2993TR-ND
R45: 220; R_0805_2012Metric; Part Number RCS0805220RFKEA; Digikey 541-10516-2-ND
TH1: 10K Thermistor; R_0805_2012Metric; Part Number ‎NB12K00103KBB; Digikey 478-NB12K00103KBBCT-ND
U1: P9242-R; QFN40P600X600X100-49N; Part Number P9242-R
U2: AP63205; TSOT-23-6; Part Number ‎AP63205WU-7; Digikey AP63205WU-7DICT-ND
U3: LMV331; SOT-23-5; Part Number ‎LMV331IDBVR‎; Digikey 296-6633-1-ND

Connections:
+5V: C46.2, C47.2, D3.1 (K), Fan1.2, J2.1, J2.3, L2.2, U2.1 (FB)
/SCL: J2.6, R2.1, U1.15 (SCL)
/SDA: J2.4, R5.1, U1.16 (SDA)
/TS: C26.2, R20.2, TH1.1, U1.20 (TS), U3.3 (-)
/coil1: C11.2, C34.2, LX1.1, Q2.1 (S), Q3.3 (D), R30.1, U1.32 (SW_BRG2)
/coil2: C20.2, C23.2, C24.2, C25.2, C35.2, D1.2 (A), LX2.1
Earth: C1.1, C2.2, C3.1, C4.1, C5.1, C6.1, C7.1, C9.1, C12.2, C13.1, C14.1, C15.1, C16.1, C17.1, C18.1, C19.1, C21.1, C26.1, C28.1, C29.1, C30.1, C31.1, C32.1, C36.1, C37.1, C38.1, C39.1, C40.1, C41.1, C42.2, C43.2, C44.2, C46.1, C47.1, C48.1, J1.2, J1.3, J2.5, Q3.1 (S), Q4.1 (S), Q5.2 (S), Q7.2 (S), Q8.2 (S), Q9.2 (S), R7.2, R8.1, R11.2, R12.2, R19.1, R31.1, R32.1, R34.2, R36.1, R37.1, R40.1, R44.1, TH1.2, U1.2 (GND), U1.6 (GND), U1.34 (GND), U1.41 (GND), U1.49 (GND), U2.4 (GND), U3.2 (V-)
ISNS_H: C27.1, R15.1, U1.48 (CSP)
ISNS_L: C27.2, R21.1, U1.47 (CSN)
LDO18: C6.2, C13.2, U1.9 (LDO18)
LDO33: C16.2, C21.2, CHG_LED1.2 (A), FLT_LED1.2 (A), R2.2, R5.2, R17.2, R20.1, R22.1, R23.2, R35.2, R43.2, R48.2, U1.7 (LDO33), U1.12 (VDDIO), U3.5 (V+)
unnamed: C1.2, C37.2, C40.2, Q2.3 (D), Q6.1 (D), R33.2, R45.1
unnamed: C7.2, C8.2, U1.45 (IDEMI)
unnamed: C8.1, R6.1
unnamed: C9.2, R6.2, U1.46 (ISNS_OUT)
unnamed: C10.1, R37.2
unnamed: C10.2, C20.1, C23.1, C24.1, C25.1, C33.2, Q1.1 (S), Q4.3 (D), R26.1, U1.36 (SW_BRG1)
unnamed: C11.1, R36.2
unnamed: C12.1, U1.3 (PREG)
unnamed: C17.2, C22.1, U1.44 (VDEM1)
unnamed: C19.2, R11.1, R13.2, R14.1
unnamed: C22.2, R13.1
unnamed: C3.2, C29.2, C38.2, C41.2, Q1.3 (D), Q6.4 (S), R18.1, R21.2, R42.2, R45.2, U1.40 (VBRG_IN)
unnamed: C33.1, U1.37 (BST_BRG1)
unnamed: C34.1, U1.31 (BST_BRG2)
unnamed: C35.1, D2.2 (A), R34.1, R35.1
unnamed: C39.2, R1.1, R10.1, R12.1
unnamed: C45.1, L2.1, U2.5 (SW)
unnamed: C45.2, U2.6 (BST)
unnamed: C48.2, R9.1, R22.2, R24.1, U3.4
unnamed: CHG_LED1.1 (K), R4.2
unnamed: D1.1 (K), R14.2
unnamed: D2.1 (K), R1.2
unnamed: D3.2 (A), Fan1.1, Q9.3 (D)
unnamed: FLT_LED1.1 (K), R3.2
unnamed: L1.2, U1.5 (SW_S)
unnamed: Q1.2 (G), R25.1, R26.2
unnamed: Q2.2 (G), R29.1, R30.2
unnamed: Q3.2 (G), R28.1, R31.2
unnamed: Q4.2 (G), R27.1, R32.2
unnamed: Q5.3 (D), R33.1
unnamed: Q6.3 (G), R41.2, R42.1
unnamed: Q7.3 (D), R41.1
unnamed: Q8.3 (D), R16.2
unnamed: Q9.1 (G), R9.2
unnamed: R3.1, U1.10 (LED1)
unnamed: R4.1, U1.11 (LED2)
unnamed: R7.1, U1.1 (~EN)
unnamed: R17.1, R19.2, R24.2, U3.1 (+)
unnamed: R25.2, U1.38 (GH_BRG1)
unnamed: R27.2, U1.35 (GL_BRG1)
unnamed: R28.2, U1.33 (GL_BRG2)
unnamed: R29.2, U1.30 (GH_BRG2)
unnamed: R40.2, R48.1, U1.17 (ILIM/FOD)
unnamed: R43.1, R44.2, U1.18 (LED/Q-FACT)
OVP_CTL: Q8.1 (G), U1.22 (OVP_CTL)
Q_DRV1: Q5.1 (G), R8.2, U1.23 (Q_DRV1)
Q_DRV2: Q7.1 (G), R23.1, U1.24 (Q_DRV2)
VCC_5V: C4.2, C5.2, C30.2, C31.2, L1.1, U1.8 (VIN_LDO), U1.39 (DRV_VIN)
VCOIL_OV: C18.2, R10.2, R16.1, U1.19 (VCOIL)
VIN: C2.1, C14.2, C15.2, C28.2, C32.2, C36.2, C42.1, C43.1, C44.1, J1.1, R15.2, R18.2, U1.4 (VIN), U2.2 (EN), U2.3 (VIN)

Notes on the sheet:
DNP unless a it is desired to connect a pi. Why would you do that? It was thought as a potential way to temporarily store data from a Maka Niu unit. This is unlikely to be worth implementing, so just DNP
V_BRIDGE?
5V regulator
This circuit turns on the fan if the temperature rises. Hysteresis built it
Always make sure that these cap are C0G or NP0 rating. High frequency and temp changes actaully make 7XR and lower caps noisy enough to not work during charging

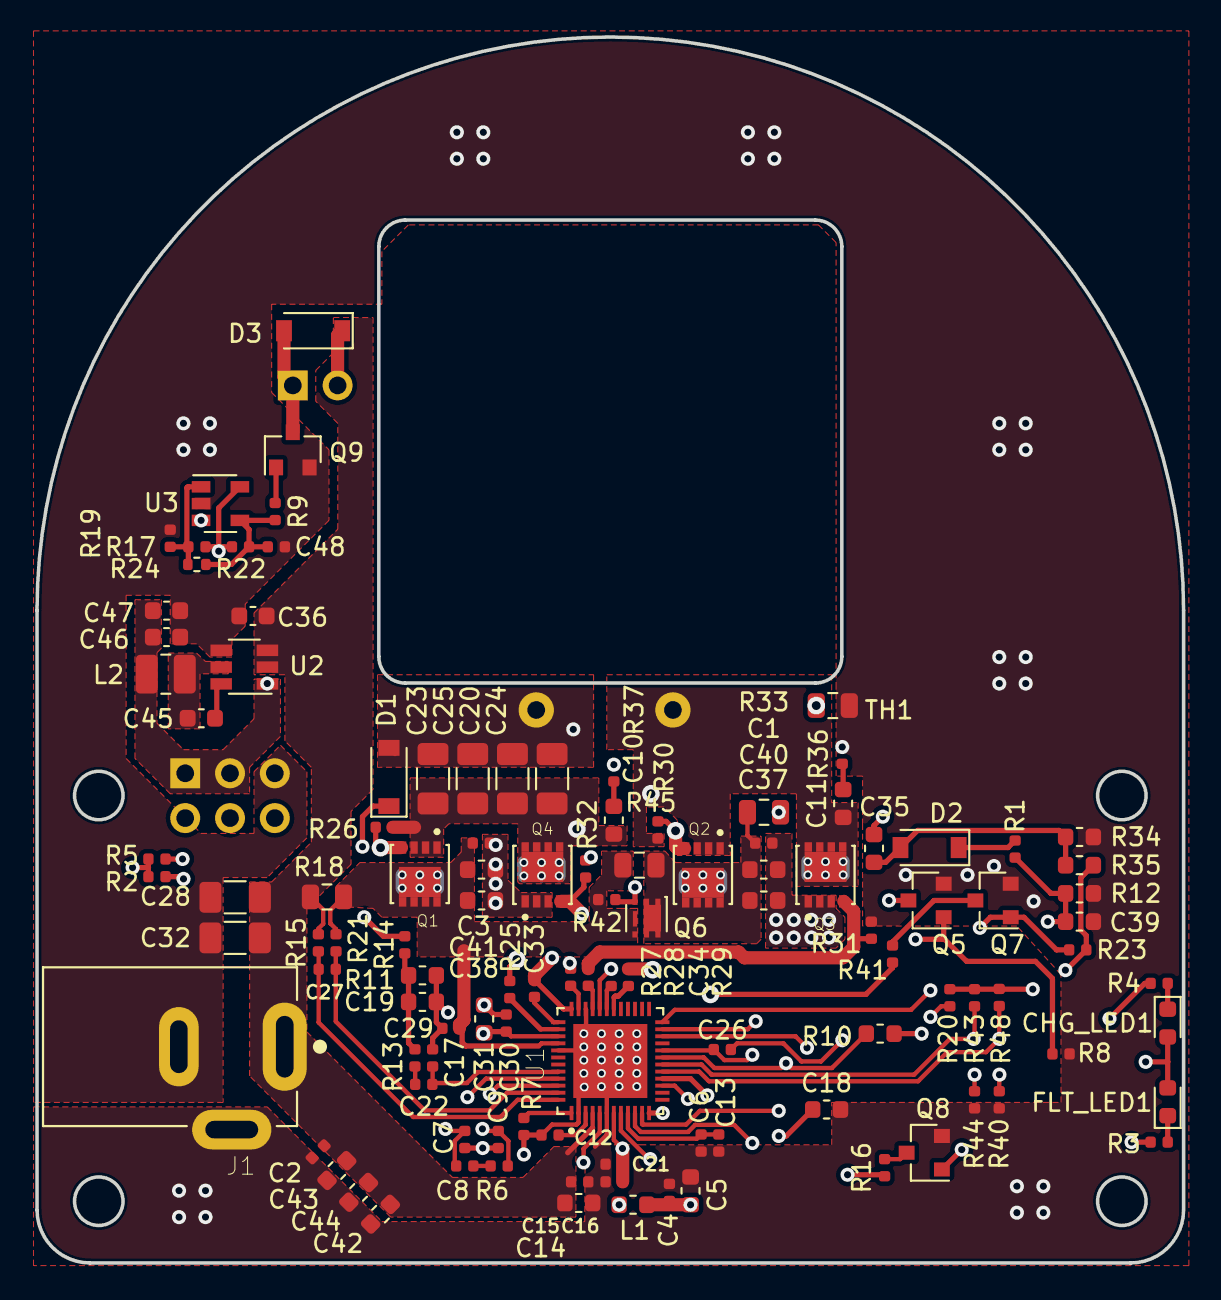
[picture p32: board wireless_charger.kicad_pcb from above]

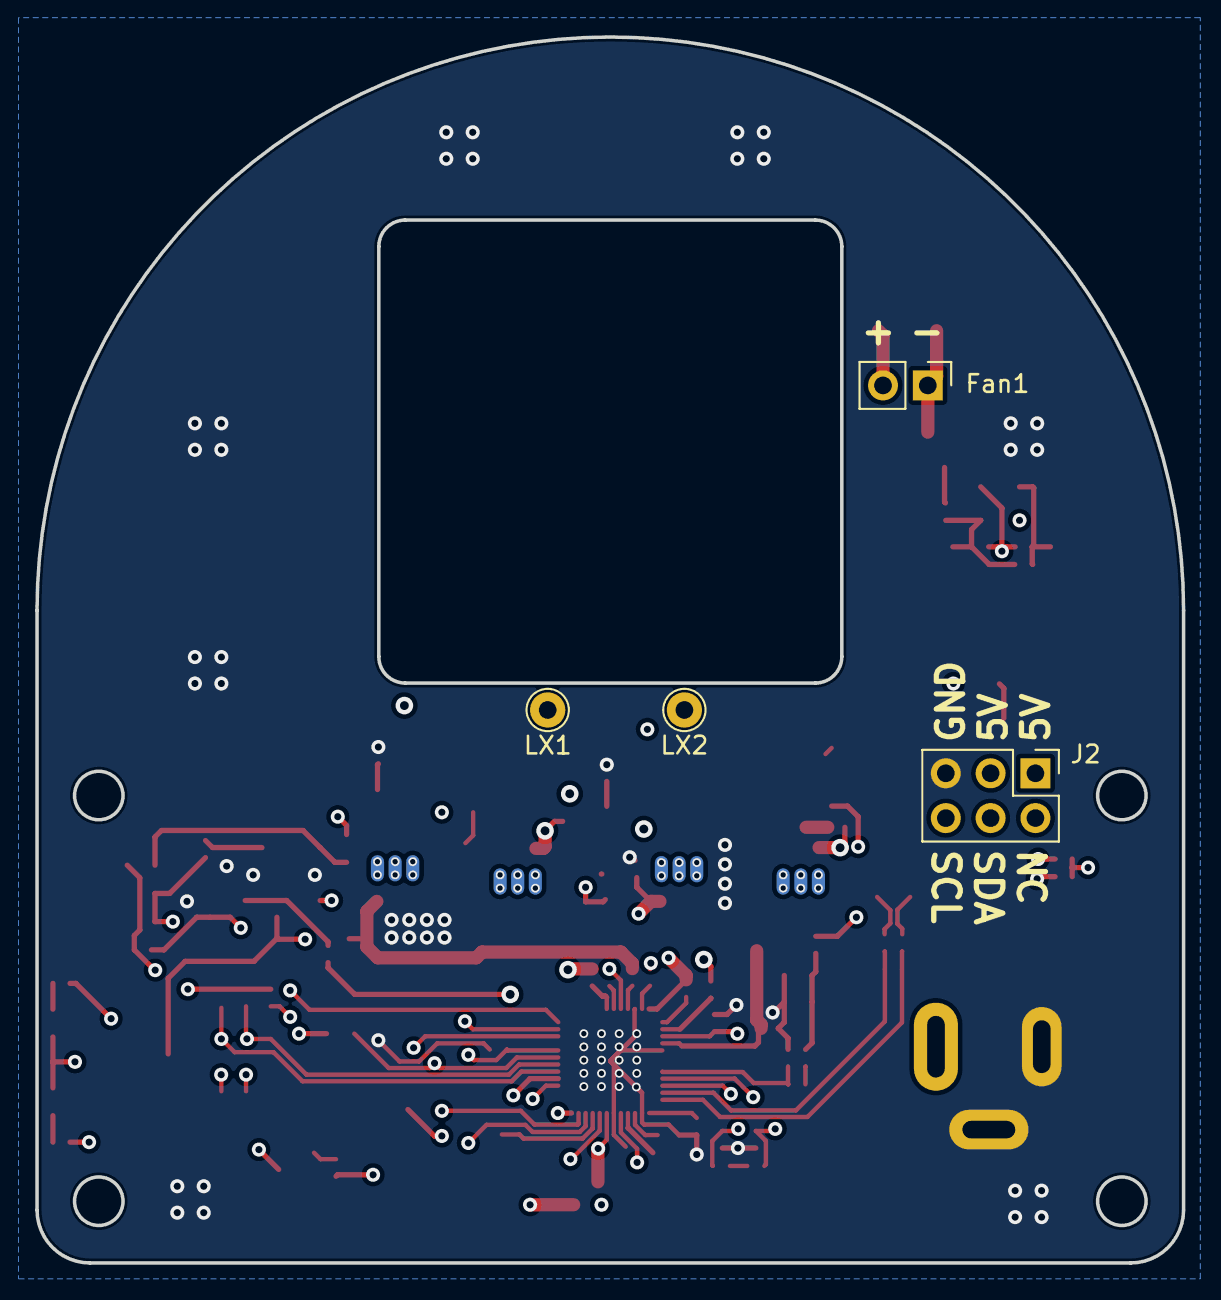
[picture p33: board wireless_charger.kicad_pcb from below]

Board: 4 copper layers, 65.0 x 69.5 mm, 117 parts (4 on the bottom side), 61 nets.

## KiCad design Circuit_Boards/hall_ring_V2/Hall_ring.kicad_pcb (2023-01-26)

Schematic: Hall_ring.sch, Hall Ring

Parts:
C1, C2, C3, C4, C5, C6, C7: 0.1uF; C_0402_1005Metric; Digikey 1276-1043-2-ND
D1: LED_RG; PinHeader_1x03_P2.00mm_Vertical; Digikey 160-1939-ND
J1: T1M-06-X-DV; SAMTEC_T1M-06-X-DV; PARTREV B
R1: 300; R_0402_1005Metric; Digikey YAG5286TR-ND
R2: 200; R_0402_1005Metric; Digikey 311-200LRTR-ND
U1, U2, U3, U4, U5, U6, U7: DRV5053_LPG; TO-92Flat; Digikey 296-DRV5032DULPGMCT-ND

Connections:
/batt: C7.1, J1.09, U7.1 (VCC)
/disable_power: J1.11, U7.3 (OUT)
/hall_1: J1.10, U1.3 (OUT)
/hall_2: J1.12, U2.3 (OUT)
/hall_3: J1.08, U3.3 (OUT)
/hall_4: J1.04, U4.3 (OUT)
/hall_5: J1.06, U5.3 (OUT)
/hall_button: J1.07, U6.3 (OUT)
GND: C1.2, C2.2, C3.2, C4.2, C5.2, C6.2, C7.2, D1.2 (Common_Cathode), J1.01, J1.S1, J1.S2, U1.2 (GND), U2.2 (GND), U3.2 (GND), U4.2 (GND), U5.2 (GND), U6.2 (GND), U7.2 (GND)
unnamed: D1.1 (Red_Anode), R1.2
unnamed: D1.3 (Green_Anode), R2.2
unnamed: J1.03, R1.1
unnamed: J1.05, R2.1
VCC: C1.1, C2.1, C3.1, C4.1, C5.1, C6.1, J1.02, U1.1 (VCC), U2.1 (VCC), U3.1 (VCC), U4.1 (VCC), U5.1 (VCC), U6.1 (VCC)

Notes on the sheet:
6 hall sensors are connected to the Pi
An additional hall sensor connects directly to the BMS

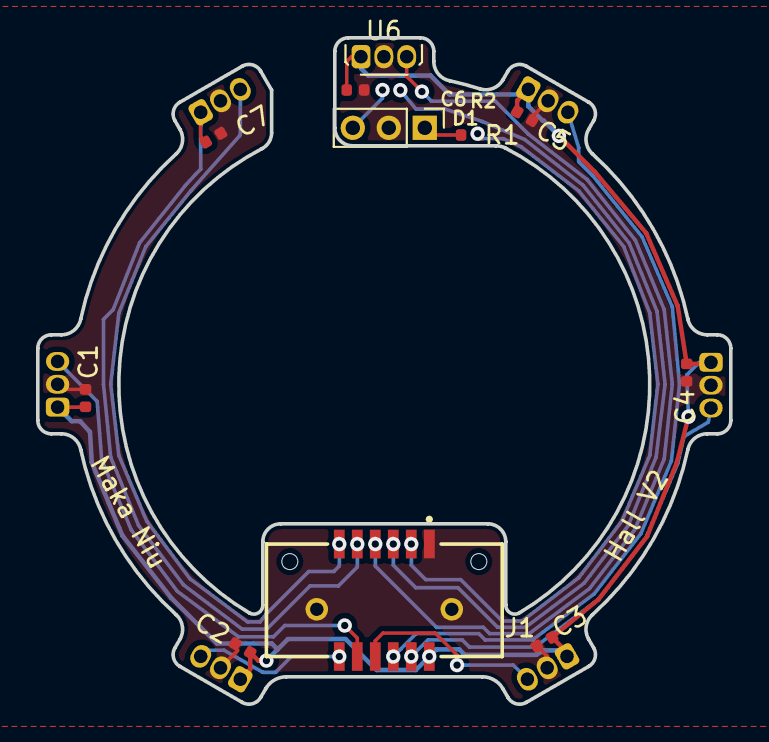
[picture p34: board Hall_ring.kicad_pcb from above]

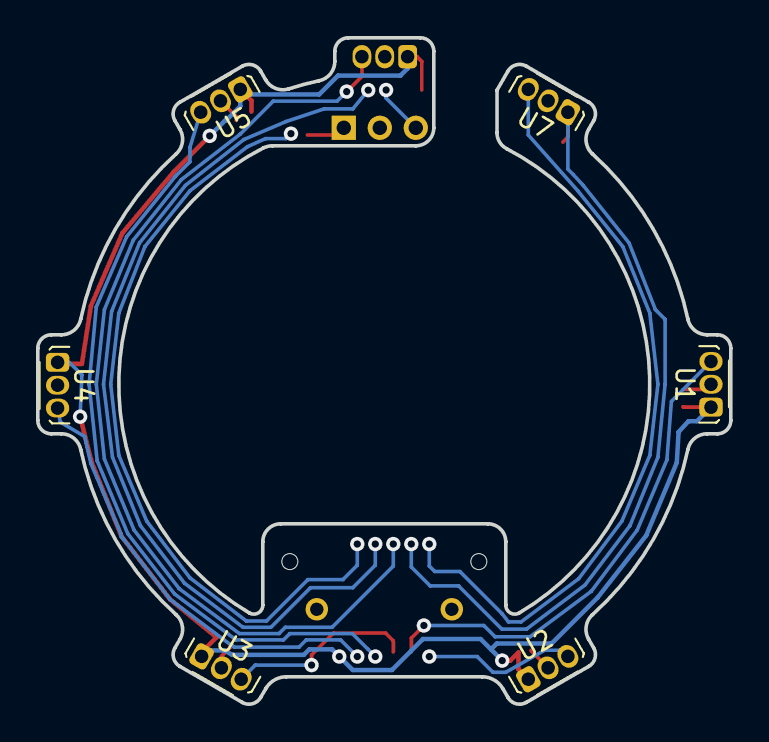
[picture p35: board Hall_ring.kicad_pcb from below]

Board: 2 copper layers, 38.5 x 37.0 mm, 18 parts (6 on the bottom side), 14 nets.

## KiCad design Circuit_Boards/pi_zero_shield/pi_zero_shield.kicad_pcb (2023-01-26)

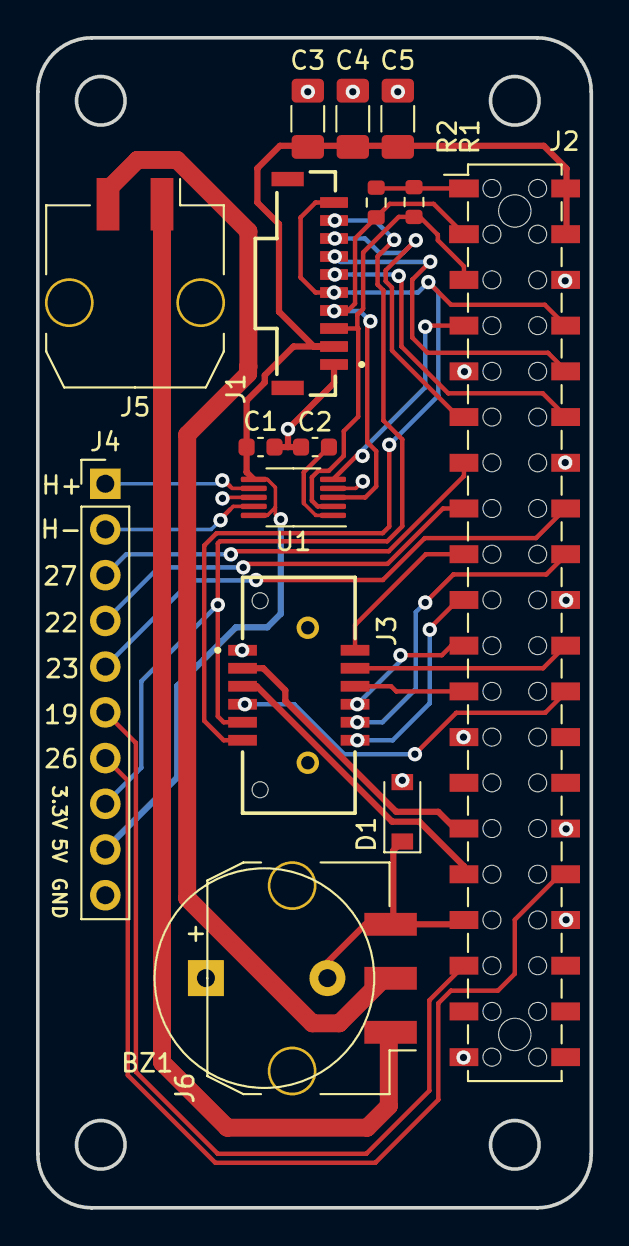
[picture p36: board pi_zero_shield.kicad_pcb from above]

Board: 2 copper layers, 30.8 x 65.0 mm, 16 parts (0 on the bottom side), 31 nets.

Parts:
BZ1: Buzzer; Buzzer_12x9.5RM7.6
C1, C2: 1.0uF; C_0603_1608Metric
C3: 10uF; C_1206_3216Metric_Pad1.33x1.80mm_HandSolder
C4, C5: DNP; C_1206_3216Metric_Pad1.33x1.80mm_HandSolder
D1: 30V 500mA; D_SOD-123
J1: T1M-10-F-SV-L; SAMTEC_T1M-10-F-SV-L
J2: Conn_02x20_Odd_Even; Pi_PinSocket_2x20
J3: T1M-06-X-DV; SAMTEC_T1M-06-X-DV
J4: Screw_Terminal_01x10; PinHeader_1x10_P2.54mm_Vertical
J5: Conn_01x02; Molex_Micro-Fit_3.0_43650-0210_1x02-1MP_P3.00mm_Horizontal
J6: Conn_01x03; Molex_Micro-Fit_3.0_43650-0310_1x03-1MP_P3.00mm_Horizontal
R1, R2: 10K; R_0603_1608Metric
U1: DRV2605LDGS; VSSOP-10_3x3mm_P0.5mm

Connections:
+3.3VP: J2.17, J3.02
+3V3: J1.09, J3.09, J4.8
+5V: C1.1, C3.1, C4.1, C5.1, J1.02, J2.2, J2.4, J4.9, U1.6 (VDD/NC), U1.10 (VDD)
+12V: J5.1, J6.1
/3.3V pullup: J2.1, R1.1, R2.1
/H+: J4.1, U1.7 (OUT+)
/H-: J4.2, U1.9 (OUT-)
/PWM_13: BZ1.2 (+), D1.1 (K), J2.33, J6.3
ENDCAP_EN: J1.06, J2.12
GND: BZ1.1 (-), C1.2, C2.2, C3.2, C4.2, C5.2, D1.2 (A), J1.01, J2.6, J2.9, J2.14, J2.20, J2.25, J2.30, J2.34, J2.39, J3.01, J4.10, U1.4 (IN/TRIG), U1.8 (GND)
GNDPWR: J5.2, J6.2
GPIO12_PWM: J2.32, J4.7
GPIO19: J2.35, J4.6
GPIO22: J2.15, J4.4
GPIO23: J2.16, J4.5
GPIO27: J2.13, J4.3
GPS_INT: J1.07, J2.10
Green_LED: J2.29, J3.03
Hall_Button: J2.24, J3.07
Hall_Image: J2.21, J3.08
Hall_M1: J2.19, J3.12
Hall_M2: J2.18, J3.10
Hall_Video: J2.22, J3.04
Hall_Wifi: J2.23, J3.06
Haptic_EN: J2.7, U1.5 (EN)
IMU_INT: J1.08, J2.11
unnamed: C2.1, U1.1 (REG)
Red_LED: J2.31, J3.05
SCL: J1.03, J2.5, R1.2, U1.2 (SCL)
SDA: J1.04, J2.3, R2.2, U1.3 (SDA)
~SHUT_DWN_SIG: J1.05, J1.10, J2.8, J3.11

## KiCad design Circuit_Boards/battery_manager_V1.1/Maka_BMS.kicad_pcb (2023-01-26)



Board: 4 copper layers, 39.0 x 35.2 mm, 95 parts (56 on the bottom side), 65 nets.

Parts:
0.0: 0.0; TruHole_Batter_Contact_Pad_with_9mm_clear
3.4: 3.4; TestPoint_THTPad_D1.5mm_Drill0.7mm
7.4_1, 7.4_2: 7.4; TruHole_Batter_Contact_Pad_with_9mm_clear
11.1: 11.1; TestPoint_THTPad_D1.5mm_Drill0.7mm
12V_OUT1: 12V_OUT; TestPoint_THTPad_D1.5mm_Drill0.7mm
C1, C7, C11, C15, C16: 10uF; C_0603_1608Metric
C2, C3, C4, C5, C13, C18, C26: 0.1uF; C_0402_1005Metric
C6, C8, C9, C12, C19, C24: 1uF; C_0402_1005Metric
C10: 1nF; C_0402_1005Metric
C14, C25: 4.7uF; C_0603_1608Metric
C17: 0.47uF; C_0402_1005Metric
C20: 15nF; C_0402_1005Metric
C21: 4.7nF; C_0402_1005Metric
C22, C23: 22uF; C_0603_1608Metric
D1, D2: 30V 3A; SMA(DO-214AC)
D3, D4: 60V 3A; D_SOD-123EP
GND_OUT1: GND_OUT; TestPoint_THTPad_D1.5mm_Drill0.7mm
J8: ‎SAM16035-ND‎; SAMTEC_T1M-10-F-SH-L-K
J9: Molex 087340-1424; Molex_87340-1424_B
L1: 4.7uH; L_1008_2520Metric
L2, L3: 10uH; Inductor5x5mm
Q1, Q2, Q3, Q6: FDC645N; SOT-23-6_mosfet
Q4, Q5: Si3483CDV; SOT-23-6_mosfet
R1, R2, R3, R4, R5, R6, R13: 1K; R_0402_1005Metric
R7, R16, R23, R34: 100K; R_0402_1005Metric
R8: 0.02; R_1206_3216Metric
R9: 15K; R_0402_1005Metric
R10, R15, R17, R32: 10K; R_0402_1005Metric
R11, R12, R14: 1M; R_0402_1005Metric
R18: 470K; R_0402_1005Metric
R19: 390K; R_0402_1005Metric
R20: 887K; R_0402_1005Metric
R21: 110K; R_0402_1005Metric
R22: 32.4K; R_0402_1005Metric
R24: 309K; R_0402_1005Metric
R25: 6.04K; R_0402_1005Metric
R26, R27: 3.01K; R_0402_1005Metric
R28: 4.99K; R_0402_1005Metric
R29: 0.25; R_1206_3216Metric
R30: 26.7K; R_0402_1005Metric
R31: 0.05; R_1206_3216Metric
R33, R37: 300K; R_0402_1005Metric
R35, R36: DNP; R_0402_1005Metric
TH1, TH2: 10K; R_0402_1005Metric
U1: AP63205; TSOT-23-6
U2, U7: TPS70933DBV; SOT-23-5
U3: BQ77915; TSSOP-24_4.4x7.8mm_P0.65mm
U4: LTC6994CS6-1; TSOT-23-6
U5: LTC4007; SSOP-24_3.9x8.7mm_P0.635mm
U6: MP3213; MSOP-8-1EP_3x3mm_P0.65mm_EP1.95x2.15mm
U8: MCP3221; SOT-23-5

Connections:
+3.3VP: C25.2, J9.7, U7.5 (OUT)
+3V3: C14.2, J8.09, J9.12, R20.2, R23.1, R35.2, R36.2, R37.1, U2.5 (OUT), U4.5 (V+), U8.1 (VDD)
+5V: C15.2, C16.2, C24.2, J8.02, L1.2, U1.1 (FB), U7.1 (IN)
+12V: C7.1, J9.1, J9.2, L3.1, R7.1, U6.6 (IN)
+15V: C11.1, C18.2, D4.1 (K), Q4.1 (D), R21.1, U5.1 (DCIN)
+BATT: 11.1.1, C23.2, D2.2 (A), R1.2, R5.2, R26.1, R31.1, R33.1
-BATT: 0.0.1, C4.1, C5.2, C8.1, C9.2, R4.2, R8.2, R16.1, R17.1, TH1.1, U3.9 (VSS), U3.10 (SRP), U3.20 (CCFG), U3.23 (CTRC), U3.24 (CTRD)
/BATT_OUT: 12V_OUT1.1, C1.2, C6.2, D1.1 (K), D2.1 (K), U1.3 (VIN), U2.1 (IN)
/GND_OUT: D1.2 (A), GND_OUT1.1, Q1.1 (D)
ENDCAP_EN: J8.06, U7.3 (EN)
Earth: C1.1, C6.1, C7.2, C11.2, C12.1, C14.1, C15.1, C16.1, C17.2, C18.1, C19.1, C21.1, C22.1, C23.1, C24.1, C25.1, C26.2, D3.2 (A), J8.01, J9.13, J9.14, Q1.3 (S), Q3.3 (S), Q6.3 (S), R9.2, R12.1, R14.1, R18.1, R19.1, R24.1, R30.1, R32.2, R34.2, TH2.1, U1.4 (GND), U2.2 (GND), U4.2 (GND), U5.2 (~CHG), U5.6 (GND), U5.7 (3C4C), U5.21 (PGND), U5.24 (SHDN), U6.4 (GND), U6.7 (FSEL), U6.9 (GND), U7.2 (GND), U8.2 (VSS)
GPS_INT: J8.07, J9.8
IMU_INT: J8.08, J9.10
unnamed: 3.4.1, R3.2
unnamed: 7.4_1.1, 7.4_2.1, R2.2
unnamed: C2.1, C3.2, R2.1, U3.6 (VC2)
unnamed: C2.2, R1.1, U3.3 (VC5), U3.4 (VC4), U3.5 (VC3)
unnamed: C3.1, C4.2, R3.1, U3.7 (VC1)
unnamed: C5.1, R4.1, U3.8 (VC0)
unnamed: C8.2, R5.1, U3.1 (VDD), U3.22 (PRES)
unnamed: C9.1, U3.2 (AVDD)
unnamed: C10.1, U6.1 (COMP)
unnamed: C10.2, R9.1
unnamed: C12.2, U6.8 (SS)
unnamed: C13.1, L1.1, U1.5 (SW)
unnamed: C13.2, U1.6 (BST)
unnamed: C17.1, R22.2, TH2.2
unnamed: C19.2, R25.1
unnamed: C20.1, C22.2, Q5.3 (S), R29.1, U5.19 (CLN)
unnamed: C20.2, R28.2, U5.18 (CLP)
unnamed: C21.2, R30.2, U5.11 (PROG)
unnamed: D3.1 (K), L2.1, Q5.1 (D), Q6.1 (D)
unnamed: D4.2 (A), L3.2, U6.5 (SW)
unnamed: L2.2, R27.1, R31.2
unnamed: Q1.2 (G), R6.2
unnamed: Q2.1 (D), Q3.1 (D)
unnamed: Q2.2 (G), R10.1, R11.2
unnamed: Q2.3 (S), R8.1, R11.1, U3.11 (SRN)
unnamed: Q3.2 (G), R12.2, R13.1
unnamed: Q4.2 (G), U5.23 (INFET)
unnamed: Q4.3 (S), R28.1, R29.2
unnamed: Q5.2 (G), U5.20 (TGATE)
unnamed: Q6.2 (G), U5.22 (BGATE)
unnamed: R7.2, U6.3 (EN)
unnamed: R10.2, U3.12 (DSG)
unnamed: R13.2, U3.13 (CHG)
unnamed: R14.2, R20.1, U4.4 (DIV)
unnamed: R15.1, TH1.2, U3.18 (TS)
unnamed: R15.2, U3.19 (VTB)
unnamed: R16.2, U3.17 (OCDP)
unnamed: R17.2, U3.16 (CBI)
unnamed: R18.2, U3.14 (LD)
unnamed: R19.2, U4.3 (SET)
unnamed: R21.2, R32.1, U6.2 (FB)
unnamed: R22.1, U5.9 (NTC)
unnamed: R24.2, U5.4 (RT)
unnamed: R25.2, U5.10 (ITH)
unnamed: R26.2, U5.15 (BAT)
unnamed: R27.2, U5.14 (CSP)
unnamed: C26.1, R33.2, R34.1, U8.3 (AIN)
SCL: J8.03, J9.5, R35.1, U8.5 (SCL)
SDA: J8.04, J9.6, R36.1, U8.4 (SDA)
~DELAYED_OFF: R6.1, U1.2 (EN), U4.6 (OUT)
~SHT_DWN_SIG: J8.05, J8.10, R37.2, U4.1 (IN)
~TS_EOC: J9.4, R23.2, U5.17 (~FLAG)

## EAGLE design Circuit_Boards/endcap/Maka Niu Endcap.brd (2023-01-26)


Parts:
BATT_CONNECT: MOLEX_87759_1450; 87759-1450; DIGI-KEY_PART_NUMBER WM18654-ND
C1: 33nF/50V; C0402; DIGI-KEY_PART_NUMBER 490-13296-1-ND
C2, C3, C5: 22nF/50V; C0402; DIGI-KEY_PART_NUMBER 490-6360-1-ND
C4, C12, C13, C15, C18, C20, C24: 1uF; C0402; DIGI-KEY_PART_NUMBER 311-1439-1-ND
C6, C14: 47nF; C0402; DIGI-KEY_PART_NUMBER 490-10702-1-ND
C7, C17, C26: 0.1uF; C0402; DIGI-KEY_PART_NUMBER 490-11917-1-ND
C8, C16: 15nF; C0402; DIGI-KEY_PART_NUMBER 490-16428-1-ND
C9: 1nF; C0402; DIGI-KEY_PART_NUMBER 732-7556-1-ND
C10, C11, C21, C22, C33: 10uF; C_0603; DIGI-KEY_PART_NUMBER 445-9015-1-ND
C19, C31: 0.1uF; C0201; DIGI-KEY_PART_NUMBER 445-7318-1-ND
C23: 0.1uF; C0201; DIGI-KEY_PART_NUMBER 1276-1318-1-ND
COIL: CHARGING_COIL
D2: 0.5A/40V/420mV; SOD-323; DIGI-KEY_PART_NUMBER 1727-5209-1-ND
FB1: 600Ω/100MHz; 0603; DIGI-KEY_PART_NUMBER 445-172898-1-ND
J1: U.FL; DIGI-KEY_PART_NUMBER A144746CT-ND
J2: KELLER_BREAKOUT; WIRES_2MM_05
J3: GPS_PROG; WIRES_2MM_02SMD
L1: 33nH/±5%/500mA; 0603; DIGI-KEY_PART_NUMBER 490-14837-1-ND
Q1, Q2: 20V/0.2A/8MHz/1.2Ω/1Vth; SOT-416FL; DIGI-KEY_PART_NUMBER RE1C002UNTCLCT-ND
R1, R3: 470; R0402; DIGI-KEY_PART_NUMBER RMCF0402JT470RCT-ND
R2: 36; R0805; DIGI-KEY_PART_NUMBER P36ADCT-ND
R4: 1k; R0402; DIGI-KEY_PART_NUMBER RMCF0402JT1K00CT-ND
R5, R6, R7, R8: 4.7k; R0402; DIGI-KEY_PART_NUMBER RMCF0402JT4K70CT-ND
R9, R10: 10k; R0402; DIGI-KEY_PART_NUMBER RMCF0402JT10K0CT-ND
R13, R14: 5.1k; R0402; DIGI-KEY_PART_NUMBER CR0402-JW-512GLFCT-ND
R15, R16: 10k; R_0603; DIGI-KEY_PART_NUMBER 311-10.0KHRCT-ND
R17, R19, R23, R27, R29, R34, R38, R39: 10k; R0402; DIGI-KEY_PART_NUMBER 541-10KATCT-ND
R22, R28, R30: NP; R0402
R33: 39.2k; R0402; DIGI-KEY_PART_NUMBER 311-39.2KLBCT-ND
RTS: THERMISTOR-2,5; RS-2,5
TP1: TP_18V; B1,27
TP2: TP_GND; B1,27
U1: P9221-R03MM_PAD; CSP52_2P64X3P94_0P4MM_03MMPAD; DIGI-KEY_PART_NUMBER 800-3932-2-ND
U2: XM1110 GPS; XM1110_GPS; DIGI-KEY_PART_NUMBER 1645-XM1110_1104311CT-ND
U3: ICM-20948; QFN40P300X300X105-24N
U4: 1.8V/100mA; SC70; DIGI-KEY_PART_NUMBER 576-2807-1-ND

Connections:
1.8V: C24.1, C26.1, Q1.1 (G), Q2.1 (G), R7.2, R8.2, TP1.TP, U3.8 (VDDIO), U3.13 (VDD), U3.22 (NCS), U4.5 (OUT)
3VBATT: BATT_CONNECT.12, D2.A
!INT: BATT_CONNECT.3, R23.1, U1.C3 (!INT)
+3V3: BATT_CONNECT.7, C12.1, C15.1, FB1.1, J2.1, L1.1, R5.2, R6.2, R9.2, R10.2, U4.1 (IN), U4.3 (EN)
AC1: C1.2, C2.2, C3.2, C5.2, C6.1, C8.1, C9.1, U1.G2 (AC1), U1.H1 (AC1_1), U1.H2 (AC1_2)
AC2: C9.2, C14.1, C16.1, COIL.B2 (2), U1.G5 (AC2), U1.H5 (AC2_1), U1.H6 (AC2_2)
ALIGNX: R16.1, U1.A2 (ALIGNX)
ALIGNY: R15.1, U1.B2 (ALIGNY)
BST1: C8.2, U1.G1 (BST1)
BST2: C16.2, U1.G6 (BST2)
COMM1: C6.2, U1.A1 (COMM1)
COMM2: C14.2, U1.A6 (COMM2)
DEN: R39.1, U1.C5 (DEN)
EOC: BATT_CONNECT.9, J2.4
GND: BATT_CONNECT.13, BATT_CONNECT.14, C4.2, C7.2, C10.2, C11.2, C12.2, C13.2, C15.2, C17.2, C18.2, C19.2, C20.2, C21.2, C22.2, C23.2, C24.2, C26.2, C31.2, C33.2, J1.1 (GND), J1.2 (GND), J2.5, R15.2, R16.2, R17.2, R22.1, R27.1, R29.1, R33.1, RTS.2, TP2.TP, U1.C1 (PGND), U1.C6 (PGND1), U1.J1 (PGND2), U1.J2 (PGND3), U1.J3 (PGND4), U1.J4 (PGND5), U1.J5 (PGND6), U1.J6 (PGND7), U2.1 (GND), U2.3 (GND), U2.4 (GND), U2.5 (GND), U2.6 (GND), U2.9 (GND), U3.11 (FSYNC), U3.18 (GND), U3.20 (RESV_20), U4.2 (GND)
GPS_INT: BATT_CONNECT.8, U2.13 (INT)
ILIM: R22.2, R38.1, U1.B4 (ILIM)
IMU_INT: BATT_CONNECT.10, U3.12 (INT1)
LC: C1.1, C2.1, C3.1, C5.1, COIL.B1 (1)
unnamed: R17.1, U1.B5 (!EN)
unnamed: D2.C, R4.2
REGOUT: C17.1, U3.10 (REGOUT)
RF_IN: J1.FEED (SIGNAL), L1.2, U2.2 (RF_IN)
RPPG: R27.2, R28.1, U1.A5 (RPPG)
RPPO: R29.2, R30.1, U1.C4 (RPPO)
RX: J3.2, R1.2, R9.1
RX0: R1.1, U2.17 (RX0)
SCL: BATT_CONNECT.5, J2.3, Q2.3 (D), R6.1, R13.1, U1.A3 (SCL), U2.11 (I2C_SCL)
SCL/SCLK: Q2.2 (S), R8.1, U3.23 (SCL/SCLK)
SDA: BATT_CONNECT.6, J2.2, Q1.3 (D), R5.1, R14.1, U1.B3 (SDA), U2.10 (I2C_SDA)
SDA/SDI: Q1.2 (S), R7.1, U3.24 (SDA/SDI)
SINK: R2.1, U1.C2 (SINK)
TS/EOC: BATT_CONNECT.4, C31.1, R19.1, RTS.1, U1.H4 (TS)
TX: J3.1, R3.2, R10.1
TX0: R3.1, U2.16 (TX0)
VBACKUP: C13.1, R4.1, U2.8 (VBACKUP)
VCC: C4.1, C7.1, FB1.2, U2.7 (VCC)
VDD5V: C18.1, U1.F1 (VDD5V)
VDD18: C19.1, C20.1, R13.2, R14.2, R19.2, R23.2, R28.2, R30.2, R34.2, R38.2, R39.2, U1.F6 (VDD18)
VOSET: R33.2, R34.1, U1.A4 (VOSET)
VOUT: BATT_CONNECT.1, BATT_CONNECT.2, C10.1, C11.1, U1.D1 (OUT), U1.D2 (OUT1), U1.D3 (OUT2), U1.D4 (OUT3), U1.D5 (OUT4), U1.D6 (OUT5), U1.G3 (RSV3), U1.H3 (RSV2)
VRECT: C21.1, C22.1, C23.1, C33.1, R2.2, U1.E1 (VRECT), U1.E2 (VRECT1), U1.E5 (VRECT2), U1.E6 (VRECT3), U1.F2 (VRECT4), U1.F3 (VRECT5), U1.F4 (VRECT6), U1.F5 (VRECT7)



Board: 6 copper layers, 26.0 x 26.0 mm, 70 parts (28 on the bottom side), 42 nets.

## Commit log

2023-01-26 imported all circuit boards from Maka-Niu into Maka-Niu-Design_Files. Additionally, KiCad porject has been cleaned, and small final changes to each design based on experiece from Maka Niu batch 2 hav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
    [Hall_ring-B_Cu.gbl, Hall_ring-B_Mask.gbs, Hall_ring-B_Silkscreen.gbo, Hall_ring-Edge_Cuts.gm1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]
2023-01-26 added instructions for post processing the endcap PCB after receiving from fab house
    [Hall_ring-B_Cu.gbl, Hall_ring-B_Mask.gbs, Hall_ring-B_Silkscreen.gbo, Hall_ring-Edge_Cuts.gm1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]
2023-04-01 cleaned up a bit and mainly added the LED board to the repo
    [Cree LED XLamp XHP50.2.STEP, LED_Heatsink_1.1.16.step, LED_board.csv, LED_board.kicad_pcb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]
2023-04-05 removed BOM and gerbers for kicad project, to ensure up to date exports
    [Hall_ring.kicad_sch, LED_board.csv, LED_board.kicad_pcb, LED_board.kicad_sch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]
2023-06-26 cosmetic fix to BMS schematic layout
    [Maka_BMS.kicad_sch]
2023-07-21 corrected part number for 10 pin BMS connector
    [Maka_BMS.kicad_sch]

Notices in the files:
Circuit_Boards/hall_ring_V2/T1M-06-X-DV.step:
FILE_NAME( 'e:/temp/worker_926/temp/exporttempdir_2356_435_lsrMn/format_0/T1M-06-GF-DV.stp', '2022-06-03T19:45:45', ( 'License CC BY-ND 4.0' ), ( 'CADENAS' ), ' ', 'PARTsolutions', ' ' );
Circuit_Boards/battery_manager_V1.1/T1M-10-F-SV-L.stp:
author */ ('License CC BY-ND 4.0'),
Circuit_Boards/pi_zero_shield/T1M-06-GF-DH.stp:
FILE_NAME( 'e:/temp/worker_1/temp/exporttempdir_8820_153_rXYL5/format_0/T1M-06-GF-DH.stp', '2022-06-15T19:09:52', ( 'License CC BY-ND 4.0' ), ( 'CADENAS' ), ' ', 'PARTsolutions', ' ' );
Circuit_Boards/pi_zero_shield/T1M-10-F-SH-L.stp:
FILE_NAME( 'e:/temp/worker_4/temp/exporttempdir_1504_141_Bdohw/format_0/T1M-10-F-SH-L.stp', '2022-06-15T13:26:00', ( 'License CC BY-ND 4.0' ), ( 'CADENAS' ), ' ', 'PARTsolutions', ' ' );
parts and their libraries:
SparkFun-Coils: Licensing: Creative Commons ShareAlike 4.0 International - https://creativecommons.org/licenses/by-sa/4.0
